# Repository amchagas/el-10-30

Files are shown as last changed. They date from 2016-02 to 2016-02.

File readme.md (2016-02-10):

This is the repository for the implementation of the electrically tunable lens 
EL-10-30, from Optotune.

Each should be controlled as follows:

 -A National instruments card is used to send voltage commands to 
   a laser diode constant current driver from Thorlabs - LD1255.
 --The driver them modulates the current going through the lens and sends
   a voltage trace (that can be transformed into current values) that can
   be read by the NI card using an analog input.

 -Other than that, the lens has a built in temperature sensor, that sends temp.
readings via I2C protocol. Because the current NI card in the lab is not able to
read such protocol, we are using a microcontroller to do that job (a Wattuino
from watterot in this case). The microcontroller communicates with the PC via 
custom serial libraries present here: https://github.com/eulerlab/SREEB, 
but in principle standard I2C libraries can be used.

a couple of notes while using the driver provided by optotune:
It is a bit hard to get the lens to heat up under the conditions we are planning
to use. 
I ran the lens for several minutes using a sinusoidal waveform @500Hz and with 
small and big amplitudes (from 40mA to 280mA and 180mA to 280mA). The system heated
up to 37°C. According to the user's manual the lens is capable of supporting
much higher temps. In any case, one needs to compensate for the change in temp,
as it affects the focal length of the lens, given a certain current. Read the lens
manual for a better description.

Running the lens @ constant DC current (280mA) also affects the temperature mildly,
again ~37°C were reached.

I'm guessing that if we are able to put some heatsinks around the lens, we should be 
able to keep the temp. from rising and avoid having to deal with changes in focal
length all together.

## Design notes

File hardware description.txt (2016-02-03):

Electrically tuned lenses (ETLs) are a good way of adding fast "z-movement" 
to microscopes, as no motors need to be used to move the entire lens set. 
From the Helmchen 2011 paper, they more or less double their scanning speed, 
from ~10Hz to ~20-30Hz.

The system works in the following manner: An ETL is placed right behind 
the microscope objective and is controlled by an laser diode or 
precise LED driver, where voltage is kept constant at 5V
and changes in current (0-300mA), change the conformation of the lens
and therefore its focal distance.

Due to aberrations introduced by this new lens in the system,
an offset lens has to be used together with the ETL.
This specific one, already comes with one, 
that can be replaced case necessary (check pdf files for instructions).

The driver chosen to drive the lens is one recommended by the manufacturer.
 From thorlabs, model LD1255R 
(laser diode constant current driver - 0.2 to 250 mA - manual attached).

The driver can be controlled with an analog signal between 0 and 5V,
so the original plan is to use an Arduino to control it. 
But the Arduino AO is not real analog, but rather PWM,
so we might have to build a low-pass filter (capacitor + resistor)
to smooth the signal. Also the AO only has 8-bit precision,
which would give us 20mA steps, and the original driver of the lens manufacturer
has 0.1mA steps. It might be interesting to use a Teensy 3.2 instead, 
since it has a true analog output and 12-bit precision, 
giving us ~1.22 mA steps. Also the board cost about the same as an Arduino.

The lens also has a temperature sensor built in, as it can get quite hot if used
for longer periods, leading to temperature drifts in the lens shape, changing
the focal distance. The idea is to hook the temperature sensor to the
microcontroller and write code to display it. We might also consider using
a heat sink on the lens, to diminish the temperature changing problem.

Driver hookup:
-The driver has a jumper to select (J2 pins, check below)
in between manual current control and
external current control (remote control with micro-controller).

PINS on J1:

1- power to board
2- ground
3- power to laser
4- external current control (0 to 5V) 
5- disable pin. They suggest that the board should always be disabled upon 
turning it on, and only them enabling the board (one can either have a
mechanical switch or have it controlled by the micro-controller).
6- laser anode (internally connected to ground)
7- laser cathode
8- monitor photodiode anode
9- Photodiode monitor output
10- Laser current monitor output

PINS on J2 (jumpers to control manual or remote current control):
If jumper in pins 1 and 2 - External current control (common referenced)
In Mode 1, the laser current is: ILD= 50 * VPIN4 (mA)
If jumper in pins 2 and 3 - External current control DISABLED

Warning: Do not operate the LD1255 without a laser diode connected because the
protection diodes can be damaged and cause the driver to fail.

The LD1255 photodiode monitor circuit only supports laser that have a photodiode
with an isolated anode. It will not support common cathode lasers such as the
CQL7825/D and CQL7840/D.

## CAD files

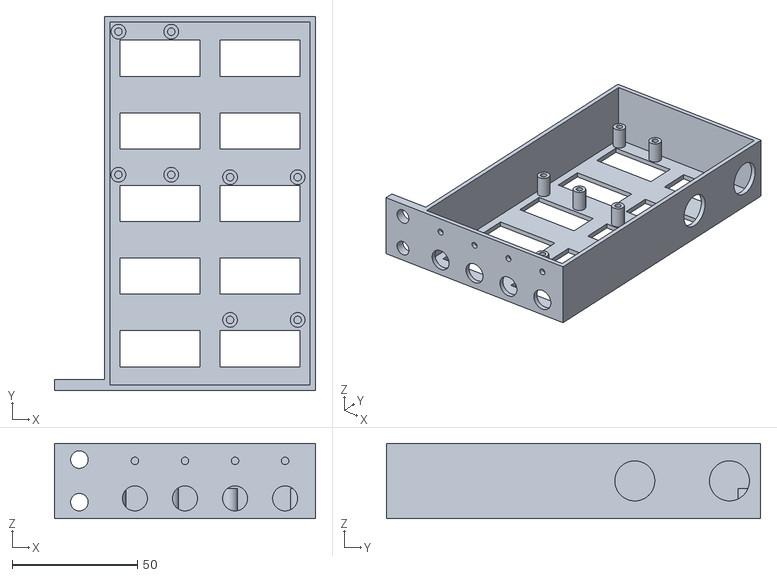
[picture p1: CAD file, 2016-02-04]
RobotControllerBox_v3.stl
104.4 x 149.4 x 30.1

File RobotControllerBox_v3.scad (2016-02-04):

wallDiam = 2.2;
tol = 0.2;

boxX = 80;
boxY = 145;
boxZ = 30;

pcbScrewDiam=5.9;
pcbScrewHole=3;
pcbScrewZ = 12;

rackX=20;
rackScrewDiam=7;
rackScrewDist=17;

cableDiam = 16;
bncDiam = 10;

ledDiam = 3;

module box(){
    difference(){
        cube([boxX+2*wallDiam,boxY+2*wallDiam,boxZ],center=true);
        translate([0,0,wallDiam]){
            cube([boxX,boxY,boxZ],center=true);}
      }//end difference
    }//end module box
    

module baseHoles(){
    numRows=5;
    numCols=2;
    for(b= [0:1:1]){
    
        for(a = [0 : 1 : numRows-1]){
            translate([b*boxX/numCols,a*boxY/numRows,-boxZ/2])
            {cube([boxX/2.5,boxY/10,10],center=true);}//end translate
            }//end for a
        }//end for b
    }

module screwTower(){
    difference(){
        cylinder(d=pcbScrewDiam,h=pcbScrewZ,center=true,$fn=50);
        cylinder(d=pcbScrewHole,h=pcbScrewZ+1,center=true,$fn=50);
    }//end difference
    }
 
module ledTower(){
    rotate([90,0,0]){
    difference(){
        cylinder(d=ledDiam+2,h=ledDiam-1,center=true,$fn=50);
        cylinder(d=ledDiam,h=ledDiam+2,center=true,$fn=50);
        }
    }
    }
module lensDriver(){
    //25.4 is one inch in mm
    xDim=25.4*2.250;
    yDim=25.4*0.830;
    screwTower();
    translate([xDim,yDim,0]){
    screwTower();}
    translate([xDim,0,0]){
    screwTower();}
    translate([0,yDim,0]){
    screwTower();}
    
    
    }

module robotShield(){
    xDim=27;
    yDim=57;
    screwTower();
    translate([xDim,yDim,0]){
    screwTower();}
    translate([xDim,0,0]){
    screwTower();}
    translate([0,yDim,0]){
    screwTower();}
    }
    

module cableHole(){
    rotate([0,90,0]){
   cylinder(d=cableDiam,h=2.5*wallDiam,center=true,$fn=50);}
}
    

module frontHoles(){  
    ports=["servo in","servo out","lens in","lens out"];
    for(b= [0:1:3]){
        translate([b*(10+bncDiam),0,0]){
            rotate([90,0,0]){
                cylinder(d=bncDiam,h=wallDiam*4,center=true,$fn=50);
            } //end rotate
        }//end translate
        rotate([90,0,0]){
            translate([b*(10+bncDiam),bncDiam/2+3,0.608]){
                text(text=ports[b],spacing=0.8,size=2.5,halign="center");
            }//end translate
        }//end rotate
                
        translate([b*(10+bncDiam),0,15]){
            rotate([90,0,0]){
                cylinder(d=ledDiam,h=wallDiam*4,center=true,$fn=50);
            } //end rotate
        }//end translate
    }//end for
}

module box2Rack(){
    
    difference(){
        cube([rackX,wallDiam*2,boxZ],center=true);
        translate([0,0,-rackScrewDist/2]){
            rotate([90,0,0]){
                cylinder(d=rackScrewDiam,h=4*wallDiam,center=true,$fn=50);}//end rotate
                }//end translate
        translate([0,0,+rackScrewDist/2]){
            rotate([90,0,0]){
                cylinder(d=rackScrewDiam,h=4*wallDiam,center=true,$fn=50);
                    }//end rotate
        }//end translate
    }//end difference

}



difference(){
box();
    translate([-boxX/4,-2*boxY/5,0]){
        baseHoles();}//end translate
    translate([(wallDiam/2)+(boxX/2),(boxY/2)-(cableDiam/2)-(2.5*cableDiam),0]){
        cableHole();}
    translate([(wallDiam/2)+(boxX/2),boxY/2-cableDiam/2-wallDiam,0]){
        rotate([0,0,00]){
        cableHole();}}
    translate([-(3*bncDiam),-boxX/1.09,-7]){
    frontHoles();}
    }//end difference

translate([-boxX/2-rackX/2-wallDiam,-boxY/2,0]){
    box2Rack();}    


    
translate([8,(-boxY/2)+26,-boxZ/3.3]){
robotShield();}

rotate([0,0,90]){
translate([(-boxX/4)+31.5,(boxY/10)+1,-boxZ/3.3]){
lensDriver();}
}

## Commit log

2016-02-03 add scad and stl files for the box where the pcbs will be contained
    [RobotControllerBox_v3.scad, RobotControllerBox_v3.stl]
2016-02-03 add arduino code to read I2C data from the temp sensor
2016-02-03 add useful pdfs: datasheet, usage manual and etc. from lens and led driver
2016-02-03 add PCB layout (built using fritzing) for a simple voltage divider plus pullup resistors , necessary to hook up the Wattuino with the lens temp sensor
    [voltage_div_plus_pull_ups.fzz]
2016-02-04 update containing box design. Screw towers are higher (pin clearance is better at the bottom, and lens driver place was turned by 90 degrees)
    [RobotControllerBox_v3.scad, RobotControllerBox_v3.stl]
2016-02-15 New lens with larger free aperture
